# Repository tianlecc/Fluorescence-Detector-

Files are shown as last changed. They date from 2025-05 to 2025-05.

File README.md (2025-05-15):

Review Assignment Due Date (https://classroom.github.com/a/AlBFWSQg)

# a14g-final-submission

    * Team Number: T16
    * Team Name: Slap Queen
    * Team Members: Tianle Chen & Sitong Li
    * Github Repository URL: https://github.com/ese5160/a14g-final-submission-s25-t16-slap-queen
    * Description of test hardware: 1. SAMD21 + WINC1500 based PCBA 2.VEML7700 light sensor; MAX31855 temperature sensor 3. WS2812B RGB LED element; 5V 1A heating pad;ESP32-S3

## 1. Video Presentation

Youtube Link:

https://youtu.be/pzpXFrXEU1Y

## 2. Project Summary

### Device Description:

* This device is a system for nucleic acid amplification and end-point fluorescence detection. It allows users to control and monitor temperature, fluorescence intensity, and test results in real time through a Wi-Fi–based web interface.
* We were inspired by the need for low-cost, portable molecular diagnostic tools suitable for point-of-care testing. Traditional fluorescence-based detection systems are often bulky and expensive, so we aimed to develop a compact, battery-powered solution that enables accessible and automated nucleic acid testing.
* The device connects to a local Wi-Fi network and communicates with a Node-RED–based web dashboard via MQTT. This enables remote control of heating, LED excitation, and data acquisition, as well as real-time visualization of temperature, fluorescence intensity, and diagnostic results.

### Device Functionality:

* Our Internet-connected device is built around a SAMD21 microcontroller and a WINC1500 Wi-Fi module, enabling MQTT-based communication with a Node-RED dashboard. Upon connecting to a Wi-Fi network, the device can receive control commands and upload data including temperature, fluorescence intensity, and diagnostic results. The Node-RED interface also supports firmware updates and system monitoring.
* The device includes several key components:

  * A **heating pad** controlled via PWM and monitored using a **MAX31855 SPI-based thermocouple sensor** for temperature feedback.
  * A  **WS2812B RGB LED** , controlled by an  **ESP32-S3 via I2C** , provides blue light excitation for fluorescent dye.
  * A **VEML7700 I2C light sensor** detects end-point fluorescence intensity in the PCR tube.
  * Power is supplied by a  **4.2V LiPo battery** , stepped up to 5V and down to 3.3V via boost and buck converters.
  * All components are housed in a custom mechanical structure that ensures proper alignment between the LED, sensor, and PCR tube.
* System-level block diagram:

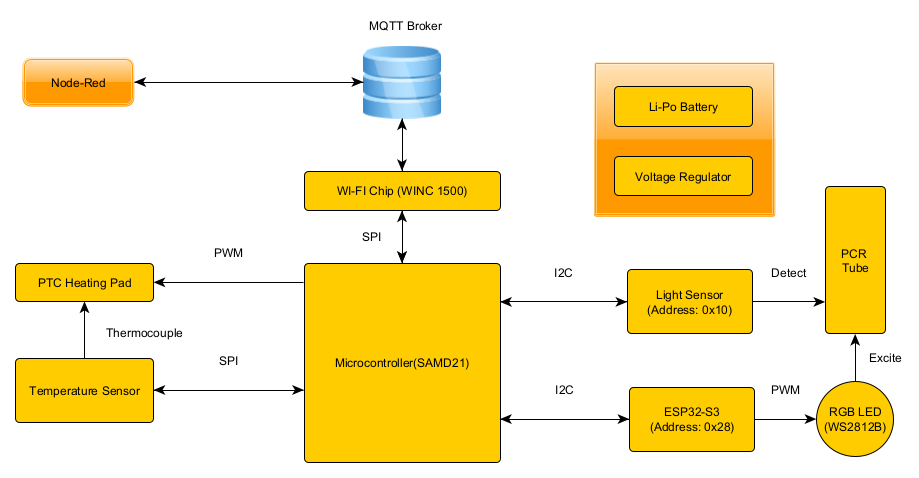
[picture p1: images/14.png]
  

### Challenges:

**Problem 1:**

The I2C bus on the PCBA was non-functional; the light sensor soldered onto the board could not be initialized.

**Solution:**
A logic analyzer showed that the SCL line was stuck high while SDA functioned normally, indicating a likely manufacturing defect. We desoldered the sensor and rerouted SDA and SCL to a breadboard, where communication worked. All I2C devices were moved off-board.

**Problem 2:**
The RGB LED could not be controlled via the PCBA; the GPIO output pin did not respond.

**Solution:**
After confirming that the control code worked on the SAMW25 dev board, we suspected a broken trace on the PCBA. As the pin lacked a test point, we used an ESP32-S3 to control the LED via PWM and sent I2C commands from the PCBA to the ESP32 for indirect control.

**Problem 3:**
The SPI-based temperature sensor only returned valid data during the first read after reset, and failed afterward.

**Solution:**
We identified a conflict between the SPI clock and FreeRTOS scheduling. Instead of delaying, we reinitialized and disabled the SPI peripheral for every temperature read, making each access act as a fresh initialization.

**Problem 4:**
The USB-to-Serial chip was incorrectly flipped in the PCB layout, making it impossible to solder.

**Solution:**
We used nearby test points for TxD and RxD to connect an external USB-to-Serial adapter and restored communication successfully.

**Problem 5:**
The J-Link debugger could not detect the PCBA because the debugger port was miswired—pin 3 was incorrectly connected to 5V instead of GND.

**Solution:**
We checked the schematic and compared it with the reference design, then used a drill to cut the 5V via, left pin 3 floating, and manually rewired it to GND using solder.

**Problem 6:**
I2C devices could be initialized under FreeRTOS, but failed to return data during normal execution.

**Solution:**
Tracealyzer revealed that the Wi-Fi task consumed most CPU time. After increasing the priority of the I2C task, communication worked reliably.

### Prototype Learnings:

* **What lessons did you learn by building and testing this prototype?**

  We learned the critical importance of validating hardware interfaces—especially I2C and SPI—early in the prototyping process, ideally with external dev boards and logic analyzers before committing to custom PCB designs. We also gained experience in designing modular firmware using FreeRTOS and understanding how task priorities and peripheral initialization timing affect system behavior. Moreover, we realized the value of including test points and debugging access for every critical signal.
* **What would you do differently if you had to build this device again?**

  If we were to build the device again, we would revise the PCB layout to ensure all important I/O pins have test points, avoid flipping parts during layout without clear markings, and double-check all power and signal routing. We would also consider moving RGB LED control off the main MCU from the beginning to simplify timing constraints. Finally, we would design the system with more flexible debugging and firmware update paths, such as integrated USB-to-serial and software-controlled SPI/I2C reinitialization.

### Next Steps & Takeaways:

* **What steps are needed to finish or improve this project?**
  To improve the project, we plan to redesign the PCB to address hardware limitations such as improper I2C routing, missing test points, and misoriented components. We will not only add test points for I2C and SPI lines but also include external port connectors to facilitate easier debugging. From a firmware perspective, instead of only displaying the end-point fluorescence result, we will implement real-time fluorescence intensity curve plotting to provide users with more informative and traceable data. We also plan to replace the 4.2V LiPo battery with a 12V power adapter, since the current battery cannot reliably support heating functions for extended use—a fresh battery only lasts for about 1.5 hours over 5–6 uses. Furthermore, we aim to improve system reliability by refining power management and integrating a more robust firmware update mechanism.
* **What did you learn in ESE5160 through the lectures, assignments, and this course-long prototyping project?**
  One of the most valuable lessons from ESE5160 was learning to design and implement a bootloader. Like a gatekeeper, the bootloader allows for crucial pre-checks before launching the main application, which helps avoid hard-to-diagnose initialization issues and enables wireless firmware updates with greater flexibility and safety. Beyond the technical skills, the most impactful takeaway was developing a problem-solving and debugging mindset. Through observing the TAs, I learned that systematic debugging is a logical process driven by experience—knowing what to check first and why. This course gave us not just the tools, but the thinking framework to face real-world engineering challenges with confidence.

### Project Links:

Node Red backend:

http://52.151.18.200:1880/#flow/66f671320a5098f3

Node Red UI:

http://52.151.18.200:1880/ui/#!/2?socketid=uGIgYGEi1WTffyEBAABM

Altium Link:

https://upenn-eselabs.365.altium.com/designs/9CF3F784-0CCA-4230-B525-11A20F8A1D04

## 3. Hardware & Software Requirements

### Hardware Requirements:

* **HRS 01 – Power Supply**
  * ***Description:*** The device shall use a 12V DC power adapter as the primary power source. Appropriate voltage regulators (e.g., DC-DC buck converters) must supply 5V or 3.3V to the ESP32 XIAO, camera, LEDs, and ancillary components.
  * ***Status:*** We eventually switched to using a 4.2V LiPo battery and adopted a 5V boost converter and a 3.3V buck converter to power the entire development board. In A11G, we have already validated this power supply architecture through the Power System Evaluation section.
* **HRS 02 – Microcontrollers**
  * ***Description:*** The device shall use SAMW25 as the main MCU for system coordination and Wi-Fi connection. In addition, the device shall use the ESP32 XIAO as an image signal process device for image capture and processing.
  * ***Status:*** Our SAMD21 and WINC1500-based PCBA functioned as expected. Instead of using the ESP32-XIAO, I opted for the ESP32-S3 as the slave device to communicate with the PCBA via I2C, and used the ESP32 to control the RGB LED.
* **HRS 03 – Camera Module**
  * ***Description:*** An OV5640 camera module shall be integrated for capturing high-resolution fluorescence images.
  * ***Status:*** Ultimately, we did not use the ESP32-based camera solution. Instead, we opted for a combination of optical filters and the VEML7700 light sensor to detect the fluorescence intensity of the PCR tube. This I2C device simplified our initial camera-based approach while still providing sufficient performance.
* **HRS 04 – LED PCB**
  * ***Description:*** An SMD2835 blue LED array shall be mounted on a separate PCB to provide the ~470 nm excitation light for green fluorescent dyes.
  * ***Status:*** We used a single WS2812B RGB LED, with color control handled by the ESP32. During operation, the LED emits blue light to excite the fluorescent dye.
* **HRS 05 – Incubator**
  * ***Description:*** The system shall include a heater board with a temperature sensor for precise (±1°C) temperature control, typically 65°C for nucleic acid amplification.
  * ***Status:*** We successfully implemented the heating pad functionality along with its corresponding temperature control. We tested their functionality by double-checked with an IR thermometer. In this project, the temperature was ultimately set to 40°C to reduce power consumption, considering the limited capacity of the LiPo battery. However, in actual molecular detection applications, a target temperature of 65°C is still required.
* **HRS 06 – LCD Display**
  * ***Description:*** A small LCD screen (e.g., 2–4 inches) shall be integrated to show test instructions and results.
  * ***Status:*** We ultimately did not use the OLED display, as our PCBA's I2C bus encountered a manufacturing issue, which limited us to connecting I2C peripherals externally via a breadboard. Additionally, since we used an extra ESP32-S3 as an I2C slave to control the RGB LED, we decided to abandon the OLED display solution.
* **HRS 07 – I2C Communication**
  * ***Description:*** The ESP32 XIAO shall communicate final image analysis results back to the main controller via I2C. The temperature sensor shall also interface via I2C.
  * ***Status:*** The I2C bus on the PCBA encountered a manufacturing issue, so all I2C peripherals—including the VEML7700 light sensor and the ESP32-S3—were connected externally via a breadboard. Meanwhile, the temperature sensor was replaced with the MAX31855, which operates on the SPI bus. Based on tests using a logic analyzer, both the I2C and SPI buses functioned perfectly.
* **HRS 08 – Form Factor & Assembly**
  * ***Description:*** The camera module, LED PCB, and heater should fit together so that the sample area is appropriately illuminated and observed. The enclosure shall be designed for easy user access to insert/remove test samples.
  * ***Status:*** Based on our finalized peripheral device setup, all hardware components were successfully integrated and functioned as intended. A specialized mechanical design allowed the LED, light sensor, and PCR tube to be properly aligned and assembled to work effectively together.

### Software Requirements:

* **SRS 01 – Camera Capture**
  * ***Description:*** The software on the ESP32 XIAO shall capture images from the OV5640 sensor at a minimum of 1 frame per minute.
  * ***Status:*** We ultimately abandoned the camera-based solution and switched to a light sensor approach. At the end of the detection process, the MCU can, under the control of Node-RED, read the current light intensity and transmit the data back to the MCU via I2C.
* **SRS 02 – Image Processing**
  * ***Description:*** The ESP32 XIAO shall analyze the captured images to estimate fluorescence intensity.
  * ***Status:*** The final solution did not include any image processing components, as we switched to using a light sensor instead.
* **SRS 03 – Data Transfer to Main Board**
  * ***Description:*** Processed results (e.g., integer intensity values, pass/fail flags) shall be sent to the main controller via I2C within 5 seconds (±2s) after analysis.
  * ***Status:*** Our MCU includes both I2C and SPI buses. The I2C bus is used to transmit commands from the MCU to control the RGB LED and to read light intensity, as well as to receive light intensity data from the light sensor. The SPI bus is used to send commands from the MCU to read the current temperature and to receive the corresponding temperature data. Before integrating the peripherals, we tested both buses using a logic analyzer, and all functions worked as expected.
* **SRS 04 – Temperature Monitoring & Control**
  * ***Description:*** The software shall poll the incubator's temperature sensor every 5 seconds (±1s) and maintain the heating element at the setpoint (e.g., 65°C ±1°C).
  * ***Status:*** As mentioned in SRS03, we achieved real-time temperature feedback control of the heating pad using a SPI-based temperature sensor. With a proportional (P) control strategy, we were able to maintain the operating temperature of the heating pad within a ±1°C error range.
* **SRS 05 – LED Activation**
  * ***Description:*** The software shall activate the SMD2835 blue LED(s) for a specified duration before image capture, ensuring stable fluorescence excitation.
  * ***Status:*** In the final implementation, we used the I2C bus to control the ESP32-S3, which in turn managed the RGB LED element. The color control of the RGB LED was achieved through PWM on the ESP32, and we used the Arduino framework to implement the LED control functionality.
* **SRS 06 – Display & UI**
  * ***Description:*** The main controller shall display test status and results on a small LCD screen and offer a smartphone web UI to view the same results.
  * ***Status:*** In the final implementation, we designed a Node-RED-based webpage that can display the current temperature, detected fluorescence intensity, test result (POSITIVE/NEGATIVE), and the current software version in real time. The webpage also provides control functions for the device. Due to hardware issues, we ultimately did not use the OLED display.
* **SRS 07 – Connectivity**
  * ***Description:*** The device shall transmit final test results over Wi-Fi to a secure server or phone application.
  * ***Status:*** We set up an MQTT virtual machine and enabled the MCU to be controlled via the Node-RED webpage once connected to Wi-Fi. This control includes firmware updates as well as the operation of actuators and sensors.
* **SRS 08 – Low Power / Idle Mode**
  * ***Description:*** The system shall enter a low-power state when inactive for more than 2 minutes and resume normal operation upon user interaction or next scheduled test cycle.
  * ***Status:*** By adjusting the priority of FreeRTOS tasks and enabling FreeRTOS idle mode, we successfully achieved low-power operation when the device is powered on but not actively running tasks. Using Tracealyzer, we were able to analyze the MCU's task execution and system behavior.

## 4. Project Photos & Screenshots

The final project:



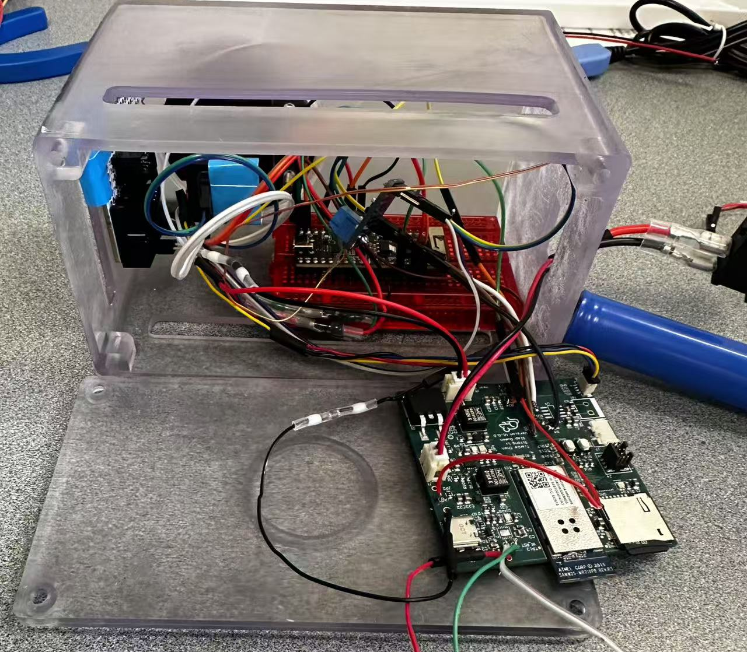
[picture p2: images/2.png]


Standalone PCBA:

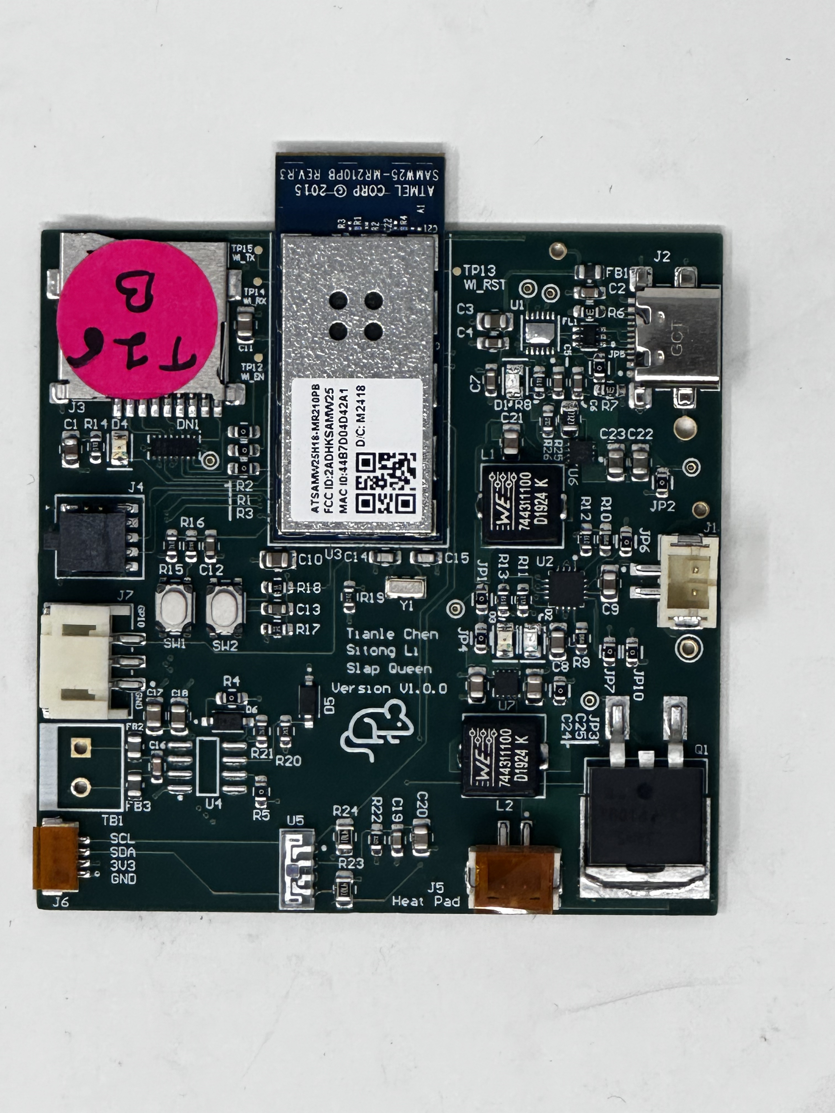
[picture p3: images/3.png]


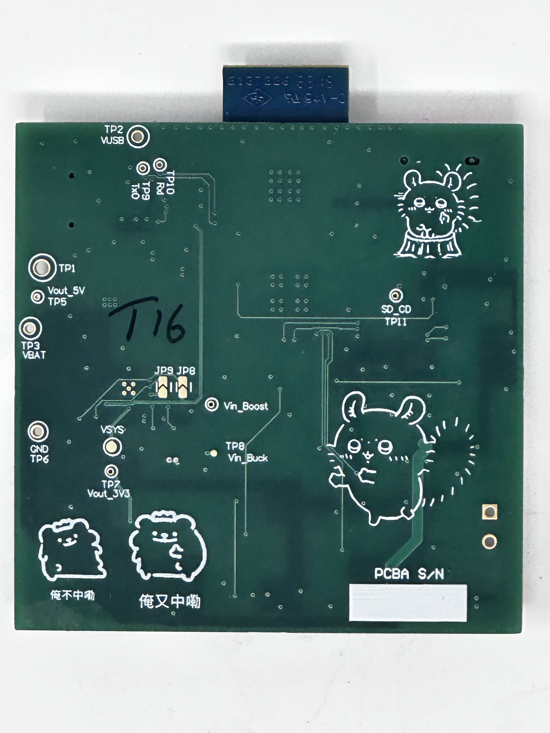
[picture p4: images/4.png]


Thermal camera image:

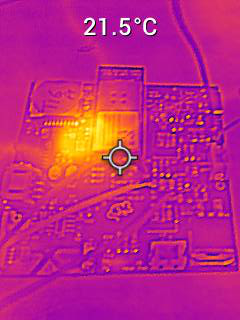
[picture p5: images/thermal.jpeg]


Altium Board Design (2D):

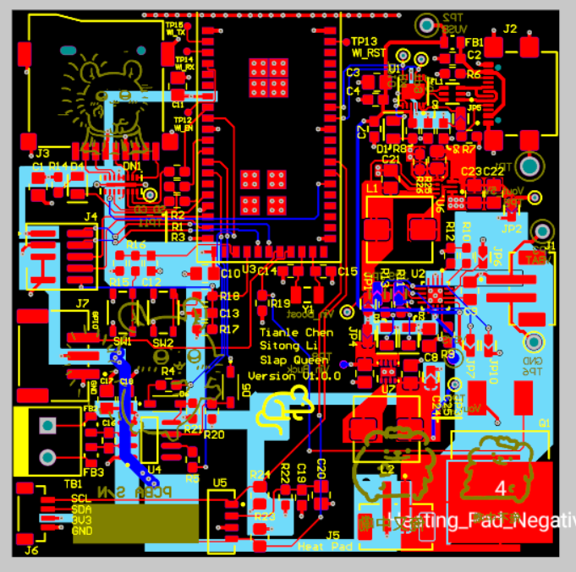
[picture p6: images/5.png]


Altium Board Design (3D):

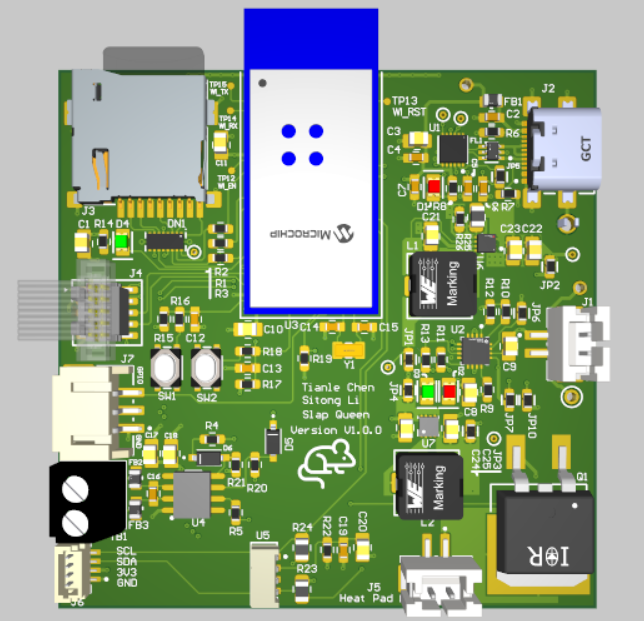
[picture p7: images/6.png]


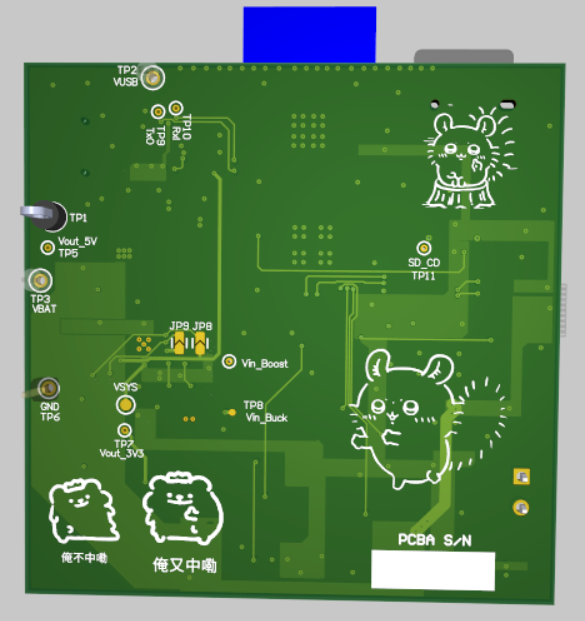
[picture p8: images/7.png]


Node-Red Dashboard:

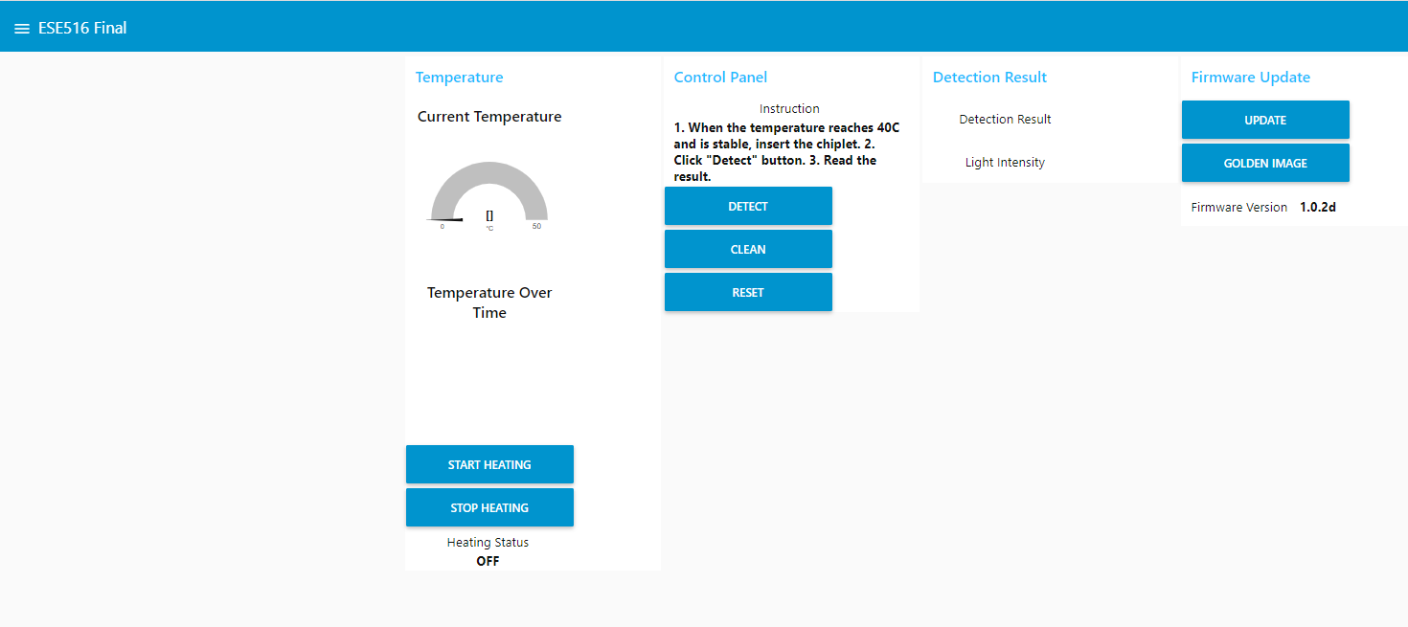
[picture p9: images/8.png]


Node-Red backend:

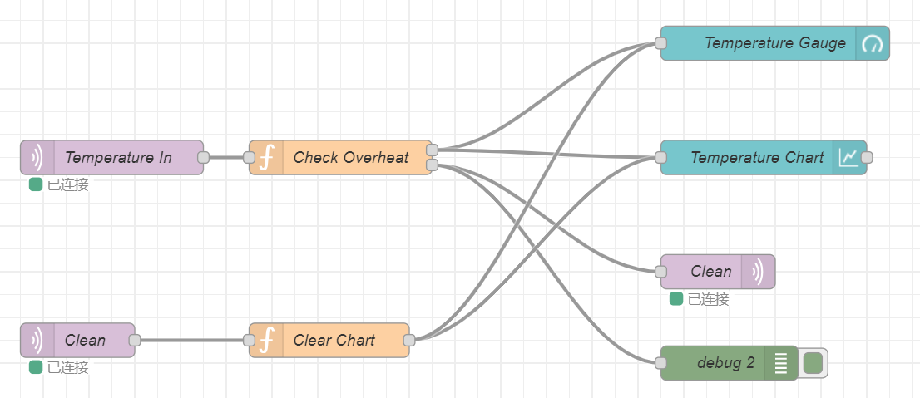
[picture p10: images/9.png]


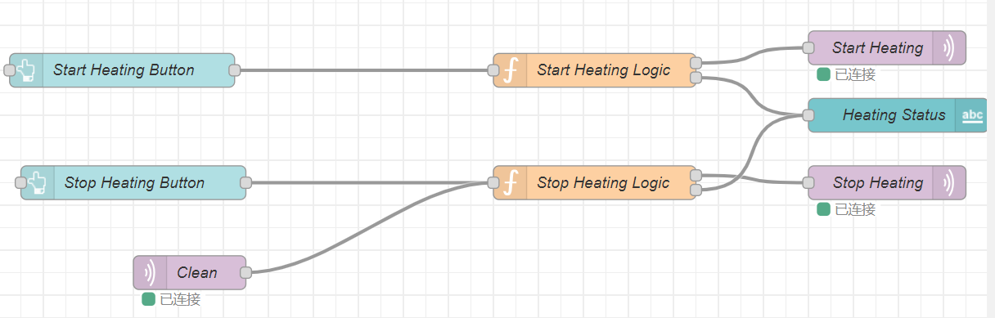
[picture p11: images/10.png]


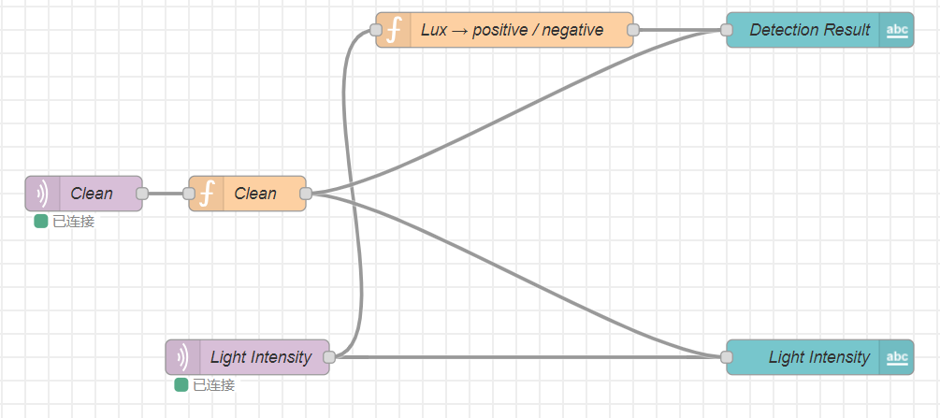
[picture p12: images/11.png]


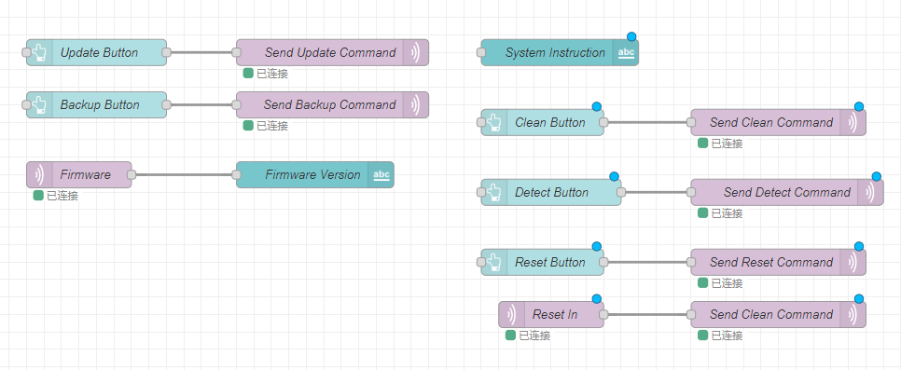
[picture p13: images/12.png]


Block Diagram:

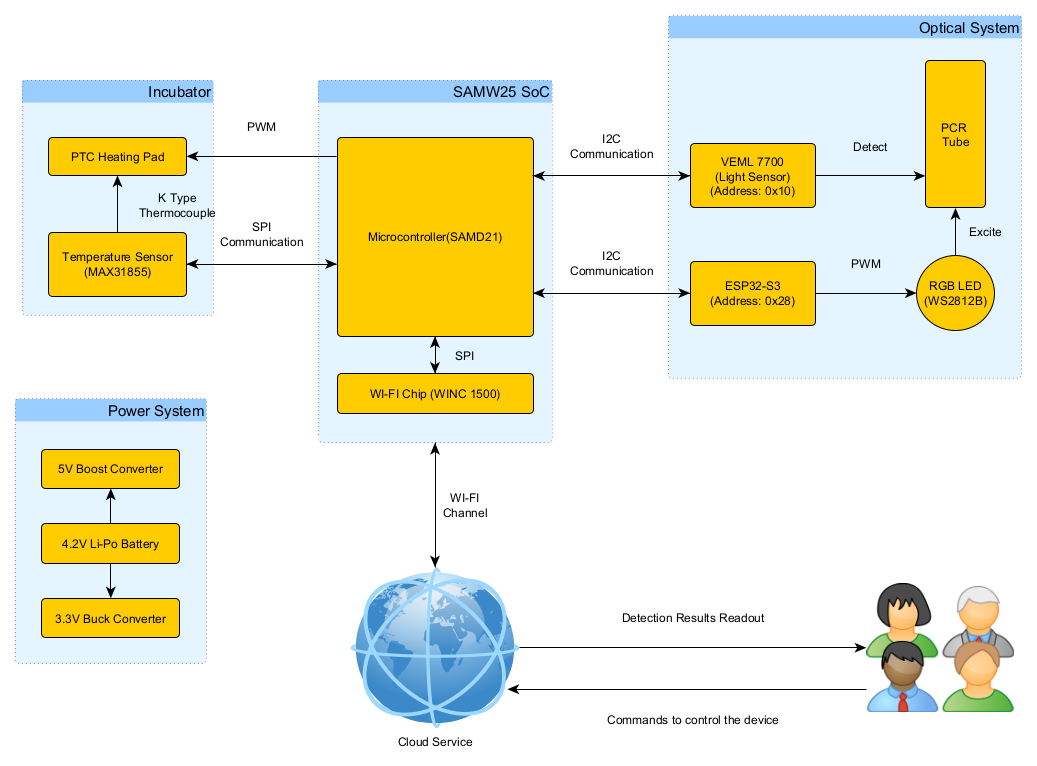
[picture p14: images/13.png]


## Codebase

- A link to your final embedded C firmware codebases

  https://github.com/ese5160/final-project-t16-slap-queen
- A link to your Node-RED dashboard code

  http://52.151.18.200:1880/#flow/66f671320a5098f3
- Links to any other software required for the functionality of your device

  ESP32-S3 Arduino firmware link:

  https://github.com/ese5160/final-project-t16-slap-queen/tree/main/esp32_i2c_slave_neopixel

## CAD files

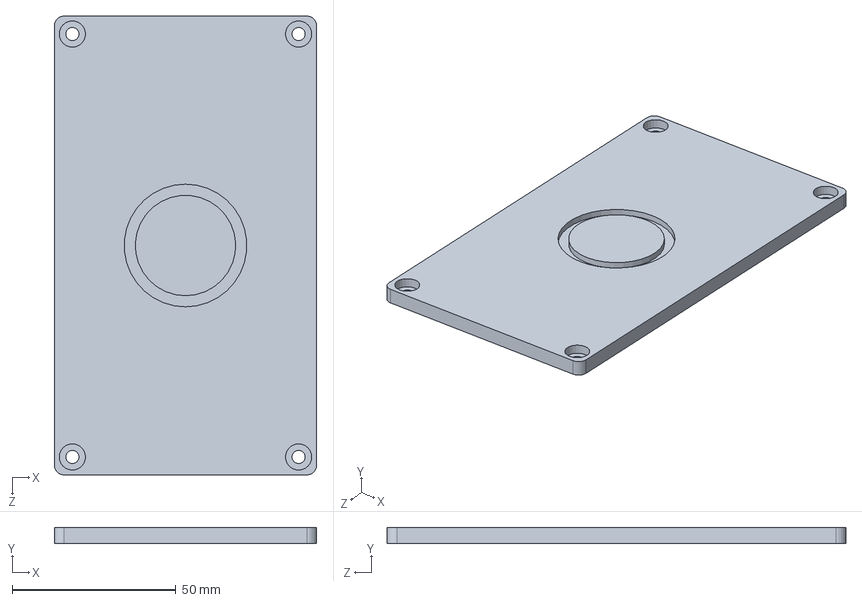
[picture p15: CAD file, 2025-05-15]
3D Models/ESE516_Part_1.SLDPRT
80.0 x 5.00 x 140.0 mm

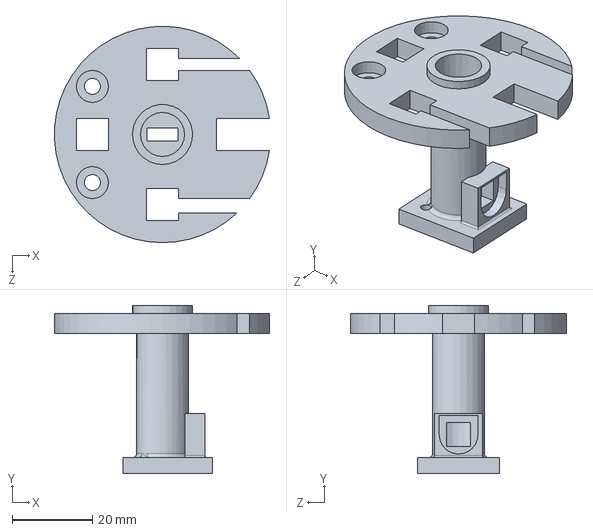
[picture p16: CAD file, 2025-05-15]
3D Models/ESE516_Part_3.SLDPRT
53.7 x 42.0 x 54.0 mm

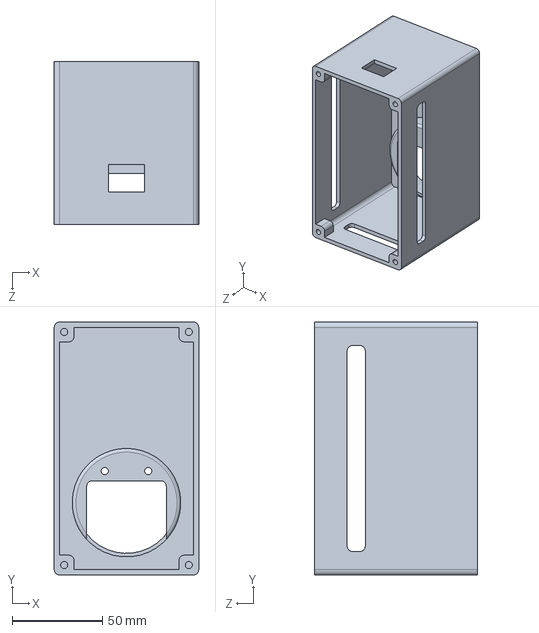
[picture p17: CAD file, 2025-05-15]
3D Models/ESE516_Part_2.SLDPRT
80.0 x 140.0 x 90.0 mm

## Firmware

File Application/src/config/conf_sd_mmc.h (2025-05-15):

/**
 * \file
 *
 * \brief SD/MMC stack configuration file.
 *
 * Copyright (c) 2016-2018 Microchip Technology Inc. and its subsidiaries.
 *
 * \asf_license_start
 *
 * \page License
 *
 * Subject to your compliance with these terms, you may use Microchip
 * software and any derivatives exclusively with Microchip products.
 * It is your responsibility to comply with third party license terms applicable
 * to your use of third party software (including open source software) that
 * may accompany Microchip software.
 *
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
 * \asf_license_stop
 *
 */
/*
 * Support and FAQ: visit <a href="https://www.microchip.com/support/">Microchip Support</a>
 */

#ifndef CONF_SD_MMC_H_INCLUDED
#define CONF_SD_MMC_H_INCLUDED

/* Define to enable the SPI mode instead of Multimedia Card interface mode */
#define SD_MMC_SPI_MODE

/* Define to enable the SDIO support */
//#define SDIO_SUPPORT_ENABLE

/* Define to enable the debug trace to the current standard output (stdio) */
//#define SD_MMC_DEBUG

/* Define to memory count */
#define SD_MMC_SPI_MEM_CNT          1

/* Select the SPI module SD/MMC is connected to */
#ifdef EXT1_SPI_MODULE /* Default configuration for Xplained Pro kit */
#  define SD_MMC_SPI                 EXT1_SPI_MODULE
#  define SD_MMC_SPI_PINMUX_SETTING  EXT1_SPI_SERCOM_MUX_SETTING
#  define SD_MMC_SPI_PINMUX_PAD0     EXT1_SPI_SERCOM_PINMUX_PAD0
#  define SD_MMC_SPI_PINMUX_PAD1     EXT1_SPI_SERCOM_PINMUX_PAD1
#  define SD_MMC_SPI_PINMUX_PAD2     EXT1_SPI_SERCOM_PINMUX_PAD2
#  define SD_MMC_SPI_PINMUX_PAD3     EXT1_SPI_SERCOM_PINMUX_PAD3

//#  define SD_MMC_CS                  EXT1_PIN_15
#define SD_MMC_CS PIN_PA07

//#  define SD_MMC_0_CD_GPIO           (EXT1_PIN_10)
#  define SD_MMC_0_CD_DETECT_VALUE   0
#else /* Dummy configuration */
#  define SD_MMC_SPI                 0
#  define SD_MMC_SPI_PINMUX_SETTING  0
#  define SD_MMC_SPI_PINMUX_PAD0     0
#  define SD_MMC_SPI_PINMUX_PAD1     0
#  define SD_MMC_SPI_PINMUX_PAD2     0
#  define SD_MMC_SPI_PINMUX_PAD3     0

#  define SD_MMC_CS                  0

#  define SD_MMC_0_CD_GPIO           0
#  define SD_MMC_0_CD_DETECT_VALUE   0
#endif

/* Define the SPI clock source */
#define SD_MMC_SPI_SOURCE_CLOCK    GCLK_GENERATOR_0

/* Define the SPI max clock */
#define SD_MMC_SPI_MAX_CLOCK       10000000 //4000000

#endif /* CONF_SD_MMC_H_INCLUDED */

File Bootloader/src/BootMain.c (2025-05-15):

/**
 * @file      BootMain.c
 * @brief     Main file for the ESE5160 bootloader. Handles updating the main application
 * @details   Main file for the ESE5160 bootloader. Handles updating the main application
 *            This version verifies the last 4 bytes of firmware files as a CRC32,
 *            then only burns (fileSize - 4) to Flash.
 * @author    
 * @date      
 * @version   
 */

/**************************************************************************
 * Includes
 **************************************************************************/
#include "conf_example.h"
#include "sd_mmc_spi.h"
#include <asf.h>
#include <string.h>

#include "ASF/sam0/drivers/dsu/crc32/crc32.h"  // For DSU-based CRC on FLASH
#include "ASF/sam0/drivers/nvm/nvm.h"
#include "SD Card/SdCard.h"
#include "SerialConsole/SerialConsole.h"
#include "Systick/Systick.h"

/**************************************************************************
 * Defines
 **************************************************************************/
#define APP_START_ADDRESS           ((uint32_t) 0xF000) ///< Start of main application. Must be address of start of main application
#define APP_START_RESET_VEC_ADDRESS (APP_START_ADDRESS + 0x04)

#define FLASH_PAGE_SIZE             (64U)
#define FLASH_ROW_SIZE              (256U)

/**************************************************************************
 * Structures and Enumerations
 **************************************************************************/
struct usart_module cdc_uart_module;   ///< Structure for UART module connected to EDBG (used for unit test output)

/**************************************************************************
 * Local Function Declaration
 **************************************************************************/
static void jumpToApplication(void);
static bool StartFilesystemAndTest(void);
static void configure_nvm(void);


/**
 * @brief Reads the specified .bin file from the SD card and writes it
 *        into the application region of Flash starting at APP_START_ADDRESS,
 *        writing the entire file from start to finish (no truncation).
 * @note  This is your older function, left intact for reference or other usage.
 */
static bool LoadFirmwareFromSDtoFlash(const char *binFilename);

/**************************************************************************
 * "Check CRC at the end" approach
 **************************************************************************/
/**
 * @brief   Calculate CRC32 for the first (fileSize - 4) bytes of the file and compare with the last 4 bytes.
 *          If they match, burn only the first (fileSize - 4) bytes into Flash.
 */
static bool CheckAndBurnCrcFirmware(const char *binFilename);

/**
 * @brief   Read the specified length (validSize) of data from the SD card and write to Flash starting at APP_START_ADDRESS.
 * @note    Write in rows of 256 bytes and pages of 64 bytes.
 */
static bool LoadFirmwareFromSDtoFlashTruncate(const char *binFilename, uint32_t validSize);

/**
 * @brief   Calculate the CRC32 (IEEE 802.3 Polynomial) for the first 'length' bytes of the file.
 * @note    DSU is not used here, because DSU is for computing the CRC of the MCU's Flash.
 *          Since we need to compute the CRC of an SD file, software or another method is used.
 */
static bool compute_file_crc32(const char *filename, uint32_t length, uint32_t *outCrc);

/**************************************************************************
 * (Optional) DSU-based function to verify firmware in Flash
 **************************************************************************/
/**
 * @brief   Verifies the CRC32 of the firmware stored in Flash (already burned).
 * @details Example usage if you want to confirm the final result in Flash.
 *          Currently not used in the main flow, but you can call after burn.
 */
static bool verify_firmware_crc(uint32_t expected_crc, uint32_t firmware_length)
{
    uint32_t computed_crc = 0xFFFFFFFFU;  // Initial value
    char buffer[64];

    // Calculate CRC32 over the application region in Flash using DSU
    if (dsu_crc32_cal(APP_START_ADDRESS, firmware_length, &computed_crc) != STATUS_OK) {
        SerialConsoleWriteString("CRC calculation failed!\r\n");
        return false;
    }
    computed_crc = ~computed_crc;

    sprintf(buffer, "Computed CRC: 0x%08X\r\n", computed_crc);
    SerialConsoleWriteString(buffer);

    // Compare computed CRC with expected value
    if (computed_crc != expected_crc) {
        sprintf(buffer, "CRC mismatch! Expected: 0x%08X, Got: 0x%08X\r\n",
                expected_crc, computed_crc);
        SerialConsoleWriteString(buffer);
        return false;
    }

    SerialConsoleWriteString("CRC match! Firmware integrity verified.\r\n");
    return true;
}

/**************************************************************************
 * Global Variables
 **************************************************************************/
char test_file_name[] = "0:sd_mmc_test.txt"; ///< Test TEXT File name
char test_bin_file[]  = "0:sd_binary.bin";   ///< Test BINARY File name
Ctrl_status status;
FRESULT res;
FATFS fs;
FIL file_object;

/**************************************************************************
 * Global Functions
 **************************************************************************/

/**
* @fn      int main(void)
* @brief   Main function for ESE5160 Bootloader Application
*
* @return  Unused (ANSI-C compatibility).
* @note    Bootloader code initiates here.
*****************************************************************************/
int main(void)
{
    /*1.) INIT SYSTEM PERIPHERALS INITIALIZATION*/
    system_init();
    delay_init();
    InitializeSerialConsole();
    system_interrupt_enable_global();

    /* Initialize SD MMC stack */
    sd_mmc_init();

    // Initialize the NVM driver
    configure_nvm();

    irq_initialize_vectors();
    cpu_irq_enable();

    // Configure DSU CRC
    dsu_crc32_init();

    SerialConsoleWriteString("ESE5160 - ENTER BOOTLOADER\r\n");

    /* END SYSTEM PERIPHERALS INITIALIZATION*/

    /*2.) STARTS SIMPLE SD CARD MOUNTING AND TEST!*/
    SerialConsoleWriteString("\x0C\n\r-- SD/MMC Card Example on FatFs --\n\r");
    if (!StartFilesystemAndTest()) {
        SerialConsoleWriteString("SD CARD failed! Check your connections. System will restart in 5 seconds...\r\n");
        delay_cycles_ms(5000);
        system_reset();
    } else {
        SerialConsoleWriteString("SD CARD mount success! Filesystem also mounted.\r\n");
    }
    /* END SIMPLE SD CARD MOUNTING AND TEST!*/


    /*3.) STARTS BOOTLOADER HERE!*/
    {
        FRESULT flagRes;
        FIL flagFile;
        bool flagUpdate = false;

        // Check if "FlagA.txt" exists
        flagRes = f_open(&flagFile, "0:FlagA.txt", FA_READ);
        if (flagRes == FR_OK) {
            flagUpdate = true;
            f_close(&flagFile);
        }

        if (flagUpdate) {
            SerialConsoleWriteString("FlagA.txt detected - updating firmware from application.bin...\r\n");

            // First, attempt to verify and burn "application.bin" (last 4 bytes contain the CRC)
            if (CheckAndBurnCrcFirmware("0:application.bin")) {
                // After a successful update, delete FlagUpdate.txt
                f_unlink("0:FlagA.txt");
            } else {
                // If that fails, fall back to using "g_application.bin"
                SerialConsoleWriteString("Error updating firmware from application.bin.\r\n");
                SerialConsoleWriteString("Falling back to g_application.bin...\r\n");

                if (LoadFirmwareFromSDtoFlash("0:g_application.bin")) {
                    f_unlink("0:FlagA.txt");
                } else {
                    SerialConsoleWriteString("Error updating firmware from g_application.bin.\r\n");
                }
            }
        } else {
            SerialConsoleWriteString("No update flag found. Go to the firmware in the flash.\r\n");
        }
    }
    /* END BOOTLOADER HERE!*/


    // 4.) DEINITIALIZE HW AND JUMP TO MAIN APPLICATION!
    SerialConsoleWriteString("ESE5160 - EXIT BOOTLOADER\r\n");
    delay_cycles_ms(100);

    DeinitializeSerialConsole();
    sd_mmc_deinit();

    // Jump to application
    jumpToApplication();

    // Should not reach here! The device should have jumped to the main firmware.
    while(1);
}

/**************************************************************************
 * Static Functions
 **************************************************************************/
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

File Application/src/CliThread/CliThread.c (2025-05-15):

/**
 * @file      CliThread.c
 * @brief     File for the CLI Thread handler. Uses FREERTOS + CLI
 * @author    Eduardo Garcia
 * @date      2020-02-15
 
 ******************************************************************************/

/******************************************************************************
 * Includes
 ******************************************************************************/
#include "CliThread.h"

#include "I2cDriver/I2cDriver.h"
#include "WifiHandlerThread/WifiHandler.h"
#include "task.h"  // For xTaskGetTickCount
#include "max31855.h"  
#include "veml7700.h"
#include "esp_i2c.h"

/******************************************************************************
 * Defines
 ******************************************************************************/

/******************************************************************************
 * Variables
 ******************************************************************************/
static const char pcWelcomeMessage[] = "FreeRTOS CLI.\r\nType Help to view a list of registered commands.\r\n";

static const CLI_Command_Definition_t xOTAUCommand = {"fw", "fw: Download a file and perform an FW update\r\n", (const pdCOMMAND_LINE_CALLBACK)CLI_OTAU, 0};
static const CLI_Command_Definition_t xResetCommand = {"reset", "reset: Resets the device\r\n", (const pdCOMMAND_LINE_CALLBACK)CLI_ResetDevice, 0};
static const CLI_Command_Definition_t xI2cScan = {"i2c", "i2c: Scans I2C bus\r\n", (const pdCOMMAND_LINE_CALLBACK)CLI_i2cScan, 0};
const CLI_Command_Definition_t xClearScreen = {CLI_COMMAND_CLEAR_SCREEN, CLI_HELP_CLEAR_SCREEN, CLI_CALLBACK_CLEAR_SCREEN, CLI_PARAMS_CLEAR_SCREEN};

// New definitions
static const CLI_Command_Definition_t xVersionCommand = {"version","version: Prints firmware version.\r\n",CLI_VersionCommand,0};
static const CLI_Command_Definition_t xTicksCommand = {"ticks","ticks: Prints the number of RTOS ticks since startup.\r\n",CLI_TicksCommand,0 };
static const CLI_Command_Definition_t xGoldCommand ={"gold","gold: Copies application.bin to g_application.bin\r\n",CLI_GoldCommand,0};
static const CLI_Command_Definition_t xTempCommand = {"temp","temp: Prints the current temperature (in Celsius) from the MAX31855.\r\n",CLI_TempCommand,0};
static const CLI_Command_Definition_t xLightCommand ={ "light", "light: Prints the last light-intensity reading (lux).\r\n",CLI_LightCommand, 0 };
static const CLI_Command_Definition_t xLedOffCommand ={ "led_off",  "led_off : Turn RGB LED off.\r\n",CLI_LedOffCommand, 0 };
static const CLI_Command_Definition_t xLedBlueCommand ={ "led_blue", "led_blue: Set LED blue.\r\n",CLI_LedBlueCommand, 0 };
static const CLI_Command_Definition_t xLedRedCommand  ={ "led_red",  "led_red : Set LED red.\r\n", CLI_LedRedCommand, 0 };
static const CLI_Command_Definition_t xLedGreenCommand ={ "led_green","led_green: Set LED green.\r\n",CLI_LedGreenCommand, 0 };


SemaphoreHandle_t cliCharReadySemaphore;  ///< Semaphore to indicate that a character has been received
SemaphoreHandle_t xRxSemaphore;

static uint8_t s_downloadBuffer[400]; //Move it outside the function as a static global variable.

/******************************************************************************
 * Forward Declarations
 ******************************************************************************/
static void FreeRTOS_read(char *character);

/******************************************************************************
 * Callback Functions
 ******************************************************************************/

/******************************************************************************
 * CLI Thread
 ******************************************************************************/
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
